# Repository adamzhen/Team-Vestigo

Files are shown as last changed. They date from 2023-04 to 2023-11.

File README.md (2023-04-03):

# Team-Vestigo

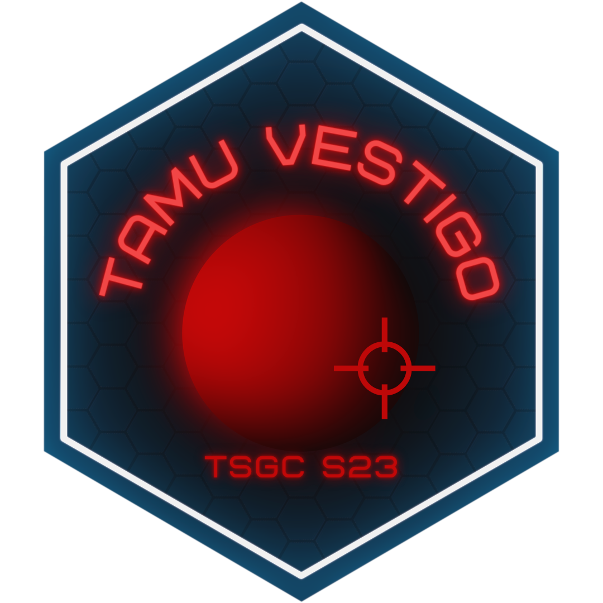
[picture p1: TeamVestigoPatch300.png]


### Crew Tracking for Space Analog Research

Since 2014, NASA’s Johnson Space Center has been using the Human Exploration Research Analog (HERA) to simulate manned space missions on Earth. We are currently developing an upgrade to HERA that will track the location and orientation of crew members in real-time, enabling researchers to efficiently analyze metrics such as how long crew members spent in certain areas or next to other crew members. The challenge is to design a device that not only has sufficient accuracy and battery life, but also a compact size and minimal crew interaction. This project is part of the Texas Space Grant Consortium Design Challenge.

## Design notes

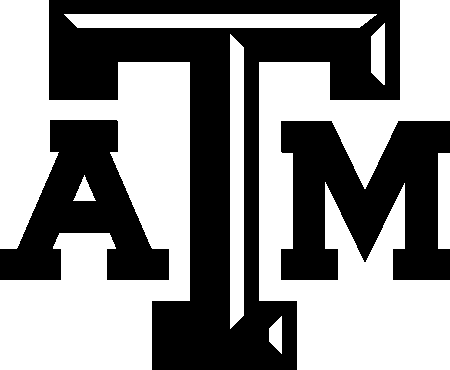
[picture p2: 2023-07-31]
PCB/TAMU(1).bmp

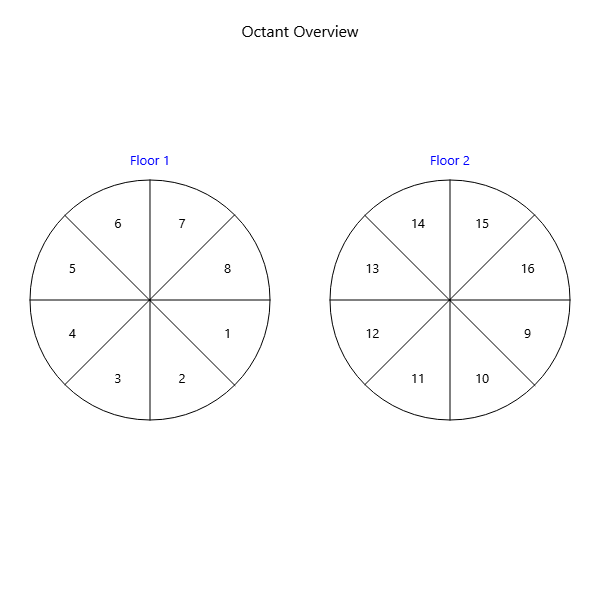
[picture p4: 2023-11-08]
GUI/QtDev/octant_reference.png

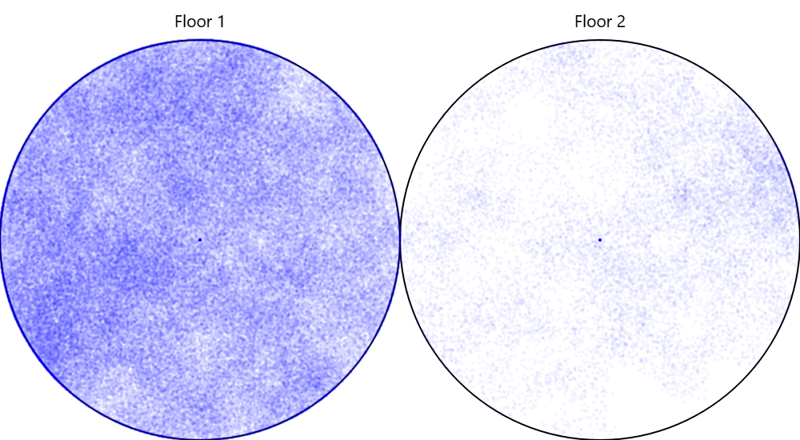
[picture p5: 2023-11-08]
GUI/QtDev/density_map.png

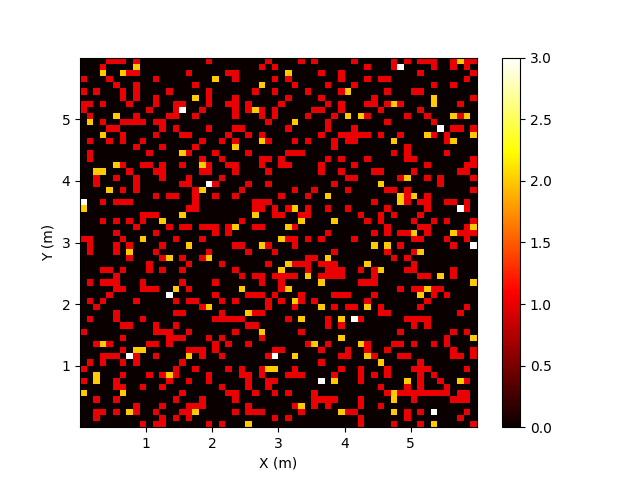
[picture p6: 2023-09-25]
GUI/QtDev/heatmap.png

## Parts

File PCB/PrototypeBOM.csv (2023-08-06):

Part | Value | Device | Package | Description | IOUT | PROD_ID | SF_ID | VALUE | VOUT
C1 | 1.0uF | 1.0UF-0402T-16V-10% | 0402-TIGHT | 1µF ceramic capacitors |  | CAP-12417 |  | 1.0uF
C2 | 0.1uF | 0.1UF-0402T-6.3V-10%-X7R | 0402-TIGHT | 0.1µF ceramic capacitors |  | CAP-14993 |  | 0.1uF
C3 | 0.1uF | C-0603 | C0603 | Ceramic Capacitors
C4 | 1.0uF | 1.0UF-0603-16V-10%-X7R | 0603 | 1µF ceramic capacitors |  | CAP-13930 |  | 1.0uF
C5 | 10uF | 10UF-0402T-6.3V-20% | 0402-TIGHT | 10.0µF ceramic capacitors |  | CAP-14848 |  | 10uF
C6 | 10uF | C-EUC0603 | C0603 | CAPACITOR, European symbol
C7 | 1.0uF | C-0603 | C0603 | Ceramic Capacitors
C8 | 10uF | C-0603 | C0603 | Ceramic Capacitors
C9 | 0.1uF | C-0603 | C0603 | Ceramic Capacitors
C10 | 1.0uF | 1.0UF-0402T-16V-10% | 0402-TIGHT | 1µF ceramic capacitors |  | CAP-12417 |  | 1.0uF
C11 | 0.1uF | C-0603 | C0603 | Ceramic Capacitors
C12 | 4.7uF | 4.7UF-0402_TIGHT-6.3V-20%-X5R | 0402-TIGHT | 4.7µF ceramic capacitors |  | CAP-14240 |  | 4.7uF
C13 | 0.1uF | 0.1UF-0402T-6.3V-10%-X7R | 0402-TIGHT | 0.1µF ceramic capacitors |  | CAP-14993 |  | 0.1uF
C14 | 0.1uF | C-0603 | C0603 | Ceramic Capacitors
C15 | 0.1uF | C-0603 | C0603 | Ceramic Capacitors
C19 | 4.7uF | 4.7UF-0603-35V-(20%) | 0603 | 4.7µF ceramic capacitors |  | CAP-14106 |  | 4.7uF
D1 | Yellow | LED-YELLOW0603 | LED-0603 | Yellow SMD LED |  | DIO-09003 |  | Yellow
D4 | 3A/10V/280mV | DIODE-SCHOTTKY-BAT60A | SOD-323 | Schottky diode |  | DIO-14072 |  | 3A/10V/280mV
D12 | RED | LED-RED0603 | LED-0603 | Red SMD LED |  | DIO-00819 |  | RED
J1 | USB Type C | USB_C_2-LAYER_PADS | USB-C-16P-2LAYER-PADS | USB Type C 16Pin Connector |  | CONN-14122
J3 | Connector | CONN_10";1X10" | Multi connection point. Often used as Generic Header-pin footprint for 0.1 inch spaced/style header connections |  | CONN-11563
J4 | Battery Connector | JST_2MM_MALE | JST-2-SMD | JST 2MM MALE RA CONNECTOR |  | CONN-11443 | PRT-08612
JP2 | JUMPER-SMT_2_NC_TRACE_SILK | JUMPER-SMT_2_NC_TRACE_SILK | SMT-JUMPER_2_NC_TRACE_SILK | Normally closed trace jumper
Q1 | S8050 | TRANSISTOR-NPN-SOT23 | SOT23 | NPN audion
Q3 | 20V/4.2A/52m?/1.4W | MOSFET_PCH-DMG2305UX-7 | SOT23-3@1 | P-channel MOSFETs |  | TRANS-14388 |  | 20V/4.2A/52m?/1.4W
Q4 | S8050 | TRANSISTOR-NPN-SOT23 | SOT23 | NPN audion
Q6 | 20V/0.2A/8MHz/1.2?/1Vth | MOSFET-NCH-RE1C002UN | SOT-416FL | N-channel MOSFETs |  | TRANS_14399 |  | 20V/0.2A/8MHz/1.2?/1Vth
Q8 | 20V/0.2A/8MHz/1.2?/1Vth | MOSFET-NCH-RE1C002UN | SOT-416FL | N-channel MOSFETs |  | TRANS_14399 |  | 20V/0.2A/8MHz/1.2?/1Vth
Q10 | 20V/0.2A/8MHz/1.2?/1Vth | MOSFET-NCH-RE1C002UN | SOT-416FL | N-channel MOSFETs |  | TRANS_14399 |  | 20V/0.2A/8MHz/1.2?/1Vth
Q12 | 20V/0.2A/8MHz/1.2?/1Vth | MOSFET-NCH-RE1C002UN | SOT-416FL | N-channel MOSFETs |  | TRANS_14399 |  | 20V/0.2A/8MHz/1.2?/1Vth
Q14 | 20V/0.2A/8MHz/1.2?/1Vth | MOSFET-NCH-RE1C002UN | SOT-416FL | N-channel MOSFETs |  | TRANS_14399 |  | 20V/0.2A/8MHz/1.2?/1Vth
Q16 | 20V/0.2A/8MHz/1.2?/1Vth | MOSFET-NCH-RE1C002UN | SOT-416FL | N-channel MOSFETs |  | TRANS_14399 |  | 20V/0.2A/8MHz/1.2?/1Vth
R1 | 1K | RESISTOR_0603_NOOUT | 0603-NO | Resistors
R3 | 1k | 1KOHM-0402T-1/16W-1% | 0402-TIGHT | 1k? resistor |  | RES-14342 |  | 1k
R4 | 2.2k | 2.2KOHM-0402T-1/16W-1% | 0402-TIGHT | 2.2k? resistor |  | RES-14341 |  | 2.2k
R5 | 2.2k | 2.2KOHM-0402T-1/16W-1% | 0402-TIGHT | 2.2k? resistor |  | RES-14341 |  | 2.2k
R6 | 2.0k | 2.0KOHM-0603-1/10W-5% | 0603 | 2k? resistor |  | RES-08296 |  | 2.0k
R7 | 10k | 10KOHM-0402T-1/16W-1% | 0402-TIGHT | 10k? resistor |  | RES-14241 |  | 10k
R8 | 10k | 10KOHM-0402T-1/16W-1% | 0402-TIGHT | 10k? resistor |  | RES-14241 |  | 10k
R9 | 5.1k | 5.1KOHM-0402T-1/16W-1% | 0402-TIGHT |  |  | RES-14340 |  | 5.1k
R10 | 5.1k | 5.1KOHM-0402T-1/16W-1% | 0402-TIGHT |  |  | RES-14340 |  | 5.1k
R11 | 1K | R-0603 | 0603
R12 | 1K | R-0603 | 0603
R13 | 1K | RESISTOR_0603_NOOUT | 0603-NO | Resistors
R14 | 1K | RESISTOR_0603_NOOUT | 0603-NO | Resistors
R15 | 10K | RESISTOR_0603_NOOUT | 0603-NO | Resistors
R16 | 2.2k | 2.2KOHM-0402T-1/16W-1% | 0402-TIGHT | 2.2k? resistor |  | RES-14341 |  | 2.2k
R17 | 2.2k | 2.2KOHM-0402T-1/16W-1% | 0402-TIGHT | 2.2k? resistor |  | RES-14341 |  | 2.2k
R18 | 2.2k | 2.2KOHM-0402T-1/16W-1% | 0402-TIGHT | 2.2k? resistor |  | RES-14341 |  | 2.2k
R19 | 2.2k | 2.2KOHM-0402T-1/16W-1% | 0402-TIGHT | 2.2k? resistor |  | RES-14341 |  | 2.2k
R20 | 2.2k | 2.2KOHM-0402T-1/16W-1% | 0402-TIGHT | 2.2k? resistor |  | RES-14341 |  | 2.2k
R21 | 2.2k | 2.2KOHM-0402T-1/16W-1% | 0402-TIGHT | 2.2k? resistor |  | RES-14341 |  | 2.2k
R22 | 2.2k | 2.2KOHM-0402T-1/16W-1% | 0402-TIGHT | 2.2k? resistor |  | RES-14341 |  | 2.2k
R23 | 2.2k | 2.2KOHM-0402T-1/16W-1% | 0402-TIGHT | 2.2k? resistor |  | RES-14341 |  | 2.2k
R24 | 2.2k | 2.2KOHM-0402T-1/16W-1% | 0402-TIGHT | 2.2k? resistor |  | RES-14341 |  | 2.2k
R25 | 2.2k | 2.2KOHM-0402T-1/16W-1% | 0402-TIGHT | 2.2k? resistor |  | RES-14341 |  | 2.2k
R34 | 1k | 1KOHM-0402T-1/16W-1% | 0402-TIGHT | 1k? resistor |  | RES-14342 |  | 1k
TP1 | 1.8V | TEST-POINT3 | PAD.03X.03 | SparkFun Test Points
U1 | 9DoF IMU | ICM-20948 | QFN24-3X3 | ICM-20948 9 Degree of Freedom IMU |  | IC-14247 |  | 9DoF IMU
U2 | MCP73831 | MCP73831 | SOT23-5 | MCP73831T Li-Ion, Li-Pol Controller |  | IC-09995
U3 | ESP-WROOM-32 | ESP-WROOM-32 | ESP-WROOM-32
U5 | DWM1000 | DWM1000 | DWM1000
U6 | 1.8V/100mA | V_REG_SP6214-1.8V | SC70 | Voltage Regulator - SP6214 |  | VREG-08428 |  | 1.8V/100mA
U7 | CH340C | CH340C | SO016 |  |  | IC-14038
U8 | XC6222B331MR-G | XC6222B331MR-G | SOT23-5 |  | 700mA | VREG-16775 |  |  | 3.3V

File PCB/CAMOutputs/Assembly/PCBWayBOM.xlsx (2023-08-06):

Item # | *Designator | *Qty | Manufacturer | *Mfg Part # | Description / Value | *Package/Footprint | Type | Your Instructions / Notes
1 | C8, C9, C3, C7, C10, C14, C15 | 7 | KYOCERA AVX | KGM15AR71C104KT | Multilayer Ceramic Capacitors MLCC - SMD/SMT 16V .1uF X7R 0603 10% | 0603 | SMD
2 | C6 | 1 | TDK | CGA3E1X7R1C105K080AC | Multilayer Ceramic Capacitors MLCC - SMD/SMT CGA 0603 16V 1uF X7R 10% AEC-Q200 | 0603 | SMD
3 | U$6, U$9 | 2 | Everlight Elec | 19-217/GHC-YR1S2/3T | Colorless transparence -40℃~+85℃ 520nm~535nm Emerald 120° 110mW 0603 Light Emitting Diodes (LED) ROHS | 0603 | SMD
4 | Q2, Q5, Q6, Q7, Q8, Q10 | 6 | ROHM Semiconductor | RE1C002UNTCL | MOSFET 1.2V Drive Nch MOSFET | SOT-416FL | SMD
5 | Q3 | 1 | Diodes Incorporated | DMG2305UX-7 | MOSFET P-Ch ENH FET -20V 52mOh -5A | SOT-23-3 | SMD
6 | D1 | 1 | Infineon Technologies | BAT60AE6327HTSA1 | Schottky Diodes & Rectifiers 10 V 3000 mA | SOD-323-2 | SMD
7 | U$11 | 1 | WCH(Jiangsu Qin Heng) | CH340B | 2Mbps Transceiver USB 2.0 SOP-16 USB ICs ROHS | SOP-16 | SMD
8 | C2, C4, C11 | 3 | Murata Electronics | GRM188R61A106ME69D | Multilayer Ceramic Capacitors MLCC - SMD/SMT 10 uF 10 VDC 20% 0603 X5R | 0603 | SMD
9 | C1,C5, C12, C16 | 4 | Wurth Elektronik | 885012000000 | Multilayer Ceramic Capacitors MLCC - SMD/SMT WCAP-CSGP 2.2uF 16V 10% | 0603 | SMD
10 | C13, C17, C19 | 3 | Murata Electronics | GRT188C81C475KE13D | Multilayer Ceramic Capacitors MLCC - SMD/SMT 4.7 uF 16 VDC 10% 0603 X6S AEC-Q200 | 0603 | SMD
11 | U5 | 1 | Qorvo | DWM3000TR13 | RF Modules UWB XCVR Module | 24 Pin 23 x 13 mm side castellated package | SMD
12 | U3 | 1 | Espressif Systems | ESP32-WROOM-32D-N4 | Multiprotocol Modules SMD Module, ESP32-D0WD, 32Mbits SPI flash, UART mode, PCB antenna | (18.00±0.10) × (25.50±0.10) × (3.10±0.10) 38 Pin Package | SMD
13 | U$5 | 1 | HEERMICR | HEERMICR | SOT-23-6 DC-DC Converters ROHS | SOT-23-6 | SMD
14 | U$12 | 1 | TDK InvenSense | ICM-20948 | IMUs - Inertial Measurement Units World's Lowest Power 9-Axis MEMS MotionTracking Device |  | QFN-24
15 | U$1, U$3 | 2 | Korean Hroparts Elec | K2-6639SP-C4SC-04 | 50mA Brick nogging SPST 100MΩ 1000000 times 250gf@±30gf 12V SMD Tactile Switches ROHS | Button | SMD
16 | U2 | 1 | Microchip Technology | MCP73831T-2ATI/OT | Battery Management Charge mgnt contr | SOT-23-5 | SMD
17 | U$2 | 1 | TDK | MLZ2012M100WT000 | Power Inductors - SMD 10 UH 20% | 805 | SMD
18 | R11, R15 | 2 | Vishay / Dale | CRCW040210K0FKEDC | Thick Film Resistors - SMD 1/16watt 10Kohms 1% Commercial Use | 0402 | SMD
19 | R9, R10, R14 | 3 | Panasonic | ERJ-3EKF1002V | Thick Film Resistors 0603 10Kohms 1% AEC-Q200 | 0603 | SMD
20 | R8 | 1 | Vishay / Draloric | RCA04021K00JNED | Thick Film Resistors - SMD RCA0402 1K0 5% 200 ET7 e3 | 0402 | SMD
21 | R1, R3, R13, R24, R25 | 5 | Panasonic | ERJ-3EKF1001V | Thick Film Resistors 0603 1Kohms 1% AEC-Q200 | 0603 | SMD
22 | R2, R4, R5, R16, R17, R18, R19, R20, R21, R22, R23, R29 | 12 | Bourns | CR0402-JW-222GLF | Thick Film Resistors - SMD 2.2K OHM 5% | 0402 | SMD
23 | R6 | 1 | Panasonic | ERJ-3EKF2001V | Thick Film Resistors - SMD 0603 2Kohms 1% AEC-Q200 | 0603 | SMD
24 | R7 | 1 | ROHM Semiconductor | SFR03EZPJ472 | Thick Film Resistors - SMD 0603 4.7Kohms 5% Anti-Sulfur AEC-Q200 | 0603 | SMD
25 | R12, R27 | 2 | Bourns | CR0402-FX-5101GLF | Thick Film Resistors - SMD 5.1K OHM 1% | 0402 | SMD
26 | Q1, Q4 | 2 | Micro Commercial Components (MCC) | MMS8050-H-TP | Bipolar Transistors - BJT NPN PURPOSE AMPLIFIER | SOT-23-3 | SMD
27 | U$8 | 1 | JST Sales America | SM02B-PASS-TB(LF)(SN) | 1x2P PA 1 2mm Male pin 2 -25℃~+85℃ 3A Surface Mount SMD,P=2mm Wire To Board / Wire To Wire Connector ROHS | SMD,P=2mm | SMD
28 | U$4 | 1 | Texas Instruments | TPS62202DBVR | Switching Voltage Regulators 1.8V Out Hi-Eff Step-Down Converter | SOT-23-5 | SMD
29 | U$7 | 1 | TECH PUBLIC | TPSMF05CT1G | SOT-323-6 | SOT-323-6 ESD Protection Devices ROHS | SMD
30 | U$10 | 1 | DEALON | USB-TYPE-C-019 | 3A 1 Surface Mount 16P Female -25℃~+85℃ Type-C SMD USB Connectors ROHS | USB-C Female Connector | SMD

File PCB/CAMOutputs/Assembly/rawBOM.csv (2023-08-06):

Qty Value Device Package Parts Description DESCRIPTION HEIGHT LCSC_DATASHEET LCSC_PART LCSC_PRICE1_EUR LCSC_ROTATION_CCW LCSC_STOCK MANUFACTURER_NAME MANUFACTURER_PART_NUMBER MOUSER_PART_NUMBER MOUSER_PRICE-STOCK PROD_ID PROPERTIES VALUE
8 CONN_01PTH_2MM 1X01_2MM J2 | J3 | J4 | J5 | J6 | J7 | J8 | J9 Single connection point. Often used as Generic Header-pin footprint for 0.1 inch spaced/style header connections
7 0.1uF 0.1UF-0603-25V-5% 0603 C8 | C9 0.1µF ceramic capacitors CAP-08604 0.1uF | C7 | C10 | C14 | C15 Capacitor General purpose SMD Capacitor https://datasheet.lcsc.com/lcsc/1809301912_YAGEO-CC0603KRX7R9BB104_C14663.pdf C14663 0 7111530 50V 100nF X7R ±10% 0603 ROHS
1 1.0uF 1.0UF-0603-16V-10%-X7R 0603 C6 1µF ceramic capacitors CAP-13930 1.0uF
2 19-217/GHC-YR1S2/3T 19-217/GHC-YR1S2/3T 19-217/GHC-YR1S2/3T U$6 | U$9
6 20V/0.2A/8MHz/1.2Ω/1Vth MOSFET-NCH-RE1C002UN SOT-416FL Q2 | Q5 | Q6 | Q7 | Q8 | Q10 N-channel MOSFETs TRANS_14399 20V/0.2A/8MHz/1.2Ω/1Vth
1 20V/4.2A/52mΩ/1.4W MOSFET_PCH-DMG2305UX-7 SOT23-3@1 Q3 P-channel MOSFETs TRANS-14388 20V/4.2A/52mΩ/1.4W
1 BAT60AE6327HTSA1 BAT60AE6327HTSA1 SOD2513X110N D1 INFINEON - BAT60AE6327HTSA1 - RECTIFIER | SCHOTTKY | 3A | 10V | SOD-323 INFINEON - BAT60AE6327HTSA1 - RECTIFIER | SCHOTTKY | 3A | 10V | SOD-323 1.1mm Infineon BAT60AE6327HTSA1 726-BAT60AE6327HTSA1 https://www.mouser.co.uk/ProductDetail/Infineon-Technologies/BAT60AE6327HTSA1?qs=OwbwYO03UsIW3Y2lCXbs8Q%3D%3D
1 CH340B CH340B SOP-16 U$11
3 C_10UF/10V_0603 C_10UF/10V_0603 C0603 C2 | C4 | C11 Capacitor General purpose SMD Capacitor https://datasheet.lcsc.com/lcsc/1810191219_Samsung-Electro-Mechanics-CL10A106KP8NNNC_C19702.pdf C19702 0 2089400 10V 10uF X5R ±10% 0603 ROHS
4 C_2.2UF/16V_0603 C_2.2UF/16V_0603 C0603 C1 | C5 | C12 | C16 Capacitor General purpose SMD Capacitor https://datasheet.lcsc.com/lcsc/1810271109_Samsung-Electro-Mechanics-CL10A225KO8NNNC_C23630.pdf C23630 0 1324345 16V 2.2uF X5R ±10% 0603 ROHS
3 C_4.7UF/16V_0603 C_4.7UF/16V_0603 C0603 C13 | C17 | C19 Capacitor General purpose SMD Capacitor https://datasheet.lcsc.com/lcsc/1810261514_Samsung-Electro-Mechanics-CL10A475KO8NNNC_C19666.pdf C19666 0 2027167 16V 4.7uF X5R ±10% 0603 ROHS
1 DWM1000 DWM1000 DWM1000 U5
1 ESP-WROOM-32 ESP-WROOM-32 ESP-WROOM-32 U3
1 HE9008M6R HE9008M6R HE9008M6R U$5
1 ICM20948 ICM20948 ICM20948 U$12
2 K2-6639SP-C4SC-04_C83206 K2-6639SP-C4SC-04_C83206 K2-6639SP-C4SC-04 U$1 | U$3 K2-6639SP-C4SC-04_C83206 button | https://datasheet.lcsc.com/lcsc/2108131530_Korean-Hroparts-Elec-K2-6639SP-C4SC-04_C83206.pdf
1 MCP73831 MCP73831 SOT23-5 U2 MCP73831T Li-Ion | Li-Pol Controller IC-09995
1 MLF2012 MLF2012 MLF2012 U$2 MLF2012
2 R_10K_0402 R_10K_0402 R0402 R11 | R15 Resistor General purpose SMD Resistor https://datasheet.lcsc.com/lcsc/2110260030_UNI-ROYAL-Uniroyal-Elec-0402WGF1002TCE_C25744.pdf C25744 0 11564817 ±1% 1/16W Thick Film Resistors 50V ±100ppm -55°C~+155°C 10kOhm 0402 ROHS
3 R_10K_0603 R_10K_0603 R0603 R9 | R10 | R14 Resistor General purpose SMD Resistor https://datasheet.lcsc.com/lcsc/2110260030_UNI-ROYAL-Uniroyal-Elec-0603WAF1002T5E_C25804.pdf C25804 0 7979018 ±1% 1/10W Thick Film Resistors 75V ±100ppm -55°C~+155°C 10kOhm 0603 ROHS
1 R_1K_0402 R_1K_0402 R0402 R8 Resistor General purpose SMD Resistor https://datasheet.lcsc.com/lcsc/2110251730_UNI-ROYAL-Uniroyal-Elec-0402WGF1001TCE_C11702.pdf C11702 0 3758383 ±1% 1/16W Thick Film Resistors 50V ±100ppm -55°C~+155°C 1kOhm 0402 ROHS
5 R_1K_0603 R_1K_0603 R0603 R1 | R3 | R13 | R24 | R25 Resistor General purpose SMD Resistor https://datasheet.lcsc.com/lcsc/2110252030_UNI-ROYAL-Uniroyal-Elec-0603WAF1001T5E_C21190.pdf C21190 0 5175299 ±1% 1/10W Thick Film Resistors 75V ±100ppm -55°C~+155°C 1kOhm 0603 ROHS
12 R_2.2K_0402 R_2.2K_0402 R0402 R2 | R4 | R5 | R16 | R17 | R18 | R19 | R20 | R21 | R22 | R23 | R29 Resistor General purpose SMD Resistor https://datasheet.lcsc.com/lcsc/2110260030_UNI-ROYAL-Uniroyal-Elec-0402WGF2201TCE_C25879.pdf C25879 0 387501 ±1% 1/16W Thick Film Resistors 50V ±100ppm -55°C~+155°C 2.2kOhm 0402 ROHS
1 R_2K_0603 R_2K_0603 R0603 R6 Resistor General purpose SMD Resistor https://datasheet.lcsc.com/lcsc/2110252130_UNI-ROYAL-Uniroyal-Elec-0603WAF2001T5E_C22975.pdf C22975 0 3372290 ±1% 1/10W Thick Film Resistors 75V ±100ppm -55°C~+155°C 2kOhm 0603 ROHS
1 R_4.7K_0603 R_4.7K_0603 R0603 R7 Resistor General purpose SMD Resistor https://datasheet.lcsc.com/lcsc/2110252130_UNI-ROYAL-Uniroyal-Elec-0603WAF4701T5E_C23162.pdf C23162 0 3103173 ±1% 1/10W Thick Film Resistors 75V ±100ppm -55°C~+155°C 4.7kOhm 0603 ROHS
2 R_5.1K_0402 R_5.1K_0402 R0402 R12 | R27 Resistor General purpose SMD Resistor https://datasheet.lcsc.com/lcsc/2110260030_UNI-ROYAL-Uniroyal-Elec-0402WGF5101TCE_C25905.pdf C25905 0 1228443 ±1% 1/16W Thick Film Resistors 50V ±100ppm -55°C~+155°C 5.1kOhm 0402 ROHS
2 S8050 TRANSISTOR-NPN-SOT23 SOT23 Q1 | Q4 NPN audion
1 SM02B_PASS_TB_LF SM02B_PASS_TB_LF SM02B_PASS_TB_LF U$8
1 TPS62202DBVR TPS62202DBVR TPS62202DBVR U$4
1 TPSMF05CT1G TPSMF05CT1G TPSMF05CT1G U$7
1 USBC19 USBC19 USBC19 U$10

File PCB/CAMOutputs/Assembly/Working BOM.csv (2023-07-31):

COMMENT | DESIGNATOR | FOOTPRINT | JLCPCB ID | Qty Value Device Package Parts Description DESCRIPTION HEIGHT LCSC_DATASHEET LCSC_PART LCSC_PRICE1_EUR LCSC_ROTATION_CCW LCSC_STOCK MANUFACTURER_NAME MANUFACTURER_PART_NUMBER MOUSER_PART_NUMBER MOUSER_PRICE-STOCK PROD_ID PROPERTIES VALUE | Qty Value Device Package Parts Description DESCRIPTION HEIGHT LCSC_DATASHEET LCSC_PART LCSC_PRICE1_EUR LCSC_ROTATION_CCW LCSC_STOCK MANUFACTURER_NAME MANUFACTURER_PART_NUMBER MOUSER_PART_NUMBER MOUSER_PRICE-STOCK PROD_ID PROPERTIES VALUE
Single connection point. Often used as Generic Header-pin footprint for 0.1 inch spaced/style header connections | J2 | 1X01_2MM |  | 8;"";"CONN_01PTH_2MM";"1X01_2MM";"J2 | 8 CONN_01PTH_2MM 1X01_2MM J2, J3, J4, J5, J6, J7, J8, J9 Single connection point. Often used as Generic Header-pin footprint for 0.1 inch spaced/style header connections
Single connection point. Often used as Generic Header-pin footprint for 0.1 inch spaced/style header connections | J3 | 1X01_2MM |  | 2;"0.1uF";"0.1UF-0603-25V-5%";"0603";"C8 | 2 0.1uF 0.1UF-0603-25V-5% 0603 C8, C9 0.1µF ceramic capacitors CAP-08604 0.1uF
Single connection point. Often used as Generic Header-pin footprint for 0.1 inch spaced/style header connections | J4 | 1X01_2MM |  | 1;"1.0uF";"1.0UF-0603-16V-10%-X7R";"0603";"C6";"1ÂµF ceramic capacitors";"";"";"";"";"";"";"";"";"";"";"";"CAP-13930";"";"1.0uF"; | 1 1.0uF 1.0UF-0603-16V-10%-X7R 0603 C6 1µF ceramic capacitors CAP-13930 1.0uF
Single connection point. Often used as Generic Header-pin footprint for 0.1 inch spaced/style header connections | J5 | 1X01_2MM |  | 2;"19-217/GHC-YR1S2/3T";"19-217/GHC-YR1S2/3T";"19-217/GHC-YR1S2/3T";"U$6 | 2 19-217/GHC-YR1S2/3T 19-217/GHC-YR1S2/3T 19-217/GHC-YR1S2/3T U$6, U$9
Single connection point. Often used as Generic Header-pin footprint for 0.1 inch spaced/style header connections | J6 | 1X01_2MM |  | 6;"20V/0.2A/8MHz/1.2Î©/1Vth";"MOSFET-NCH-RE1C002UN";"SOT-416FL";"Q2 | 6 20V/0.2A/8MHz/1.2?/1Vth MOSFET-NCH-RE1C002UN SOT-416FL Q2, Q5, Q6, Q7, Q8, Q10 N-channel MOSFETs TRANS_14399 20V/0.2A/8MHz/1.2?/1Vth
Single connection point. Often used as Generic Header-pin footprint for 0.1 inch spaced/style header connections | J7 | 1X01_2MM |  | 1;"20V/4.2A/52mÎ©/1.4W";"MOSFET_PCH-DMG2305UX-7";"SOT23-3@1";"Q3";"P-channel MOSFETs";"";"";"";"";"";"";"";"";"";"";"";"TRANS-14388";"";"20V/4.2A/52mÎ©/1.4W"; | 1 20V/4.2A/52m?/1.4W MOSFET_PCH-DMG2305UX-7 SOT23-3@1 Q3 P-channel MOSFETs TRANS-14388 20V/4.2A/52m?/1.4W
Single connection point. Often used as Generic Header-pin footprint for 0.1 inch spaced/style header connections | J8 | 1X01_2MM |  | 1;"9DoF IMU";"ICM-20948";"QFN24-3X3";"U1";"ICM-20948 9 Degree of Freedom IMU";"";"";"";"";"";"";"";"";"";"";"";"IC-14247";"";"9DoF IMU"; | 1 9DoF IMU ICM-20948 QFN24-3X3 U1 ICM-20948 9 Degree of Freedom IMU IC-14247 9DoF IMU
Single connection point. Often used as Generic Header-pin footprint for 0.1 inch spaced/style header connections | J9 | 1X01_2MM |  | 1;"BAT60AE6327HTSA1";"BAT60AE6327HTSA1";"SOD2513X110N";"D1";"INFINEON - BAT60AE6327HTSA1 - RECTIFIER | 1 BAT60AE6327HTSA1 BAT60AE6327HTSA1 SOD2513X110N D1 INFINEON - BAT60AE6327HTSA1 - RECTIFIER, SCHOTTKY, 3A, 10V, SOD-323 INFINEON - BAT60AE6327HTSA1 - RECTIFIER, SCHOTTKY, 3A, 10V, SOD-323 1.1mm Infineon BAT60AE6327HTSA1 726-BAT60AE6327HTSA1 https://www.mouser.co.uk/ProductDetail/Infineon-Technologies/BAT60AE6327HTSA1?qs=OwbwYO03UsIW3Y2lCXbs8Q%3D%3D
19-217/GHC-YR1S2/3T | U$6 | 603 | C72043 | 1;"CH340C";"CH340C";"SO016";"U7";"";"";"";"";"";"";"";"";"";"";"";"";"IC-14038";"";""; | 1 CH340C CH340C SO016 U7 IC-14038
19-217/GHC-YR1S2/3T | U$9 | 603 | C72043 | 5;"C_100NF/50V_0603";"C_100NF/50V_0603";"C0603";"C3 | 5 C_100NF/50V_0603 C_100NF/50V_0603 C0603 C3, C7, C10, C14, C15 Capacitor General purpose SMD Capacitor https://datasheet.lcsc.com/lcsc/1809301912_YAGEO-CC0603KRX7R9BB104_C14663.pdf C14663 0 7111530 50V 100nF X7R ±10% 0603 ROHS
RE1C002UNTL | Q2 | SOT-416FL | C509959 | 3;"C_10UF/10V_0603";"C_10UF/10V_0603";"C0603";"C2 | 3 C_10UF/10V_0603 C_10UF/10V_0603 C0603 C2, C4, C11 Capacitor General purpose SMD Capacitor https://datasheet.lcsc.com/lcsc/1810191219_Samsung-Electro-Mechanics-CL10A106KP8NNNC_C19702.pdf C19702 0 2089400 10V 10uF X5R ±10% 0603 ROHS
RE1C002UNTL | Q5 | SOT-416FL | C509959 | 4;"C_2.2UF/16V_0603";"C_2.2UF/16V_0603";"C0603";"C1 | 4 C_2.2UF/16V_0603 C_2.2UF/16V_0603 C0603 C1, C5, C12, C16 Capacitor General purpose SMD Capacitor https://datasheet.lcsc.com/lcsc/1810271109_Samsung-Electro-Mechanics-CL10A225KO8NNNC_C23630.pdf C23630 0 1324345 16V 2.2uF X5R ±10% 0603 ROHS
RE1C002UNTL | Q6 | SOT-416FL | C509959 | 3;"C_4.7UF/16V_0603";"C_4.7UF/16V_0603";"C0603";"C13 | 3 C_4.7UF/16V_0603 C_4.7UF/16V_0603 C0603 C13, C17, C19 Capacitor General purpose SMD Capacitor https://datasheet.lcsc.com/lcsc/1810261514_Samsung-Electro-Mechanics-CL10A475KO8NNNC_C19666.pdf C19666 0 2027167 16V 4.7uF X5R ±10% 0603 ROHS
RE1C002UNTL | Q7 | SOT-416FL | C509959 | 1;"DWM1000";"DWM1000";"DWM1000";"U5";"";"";"";"";"";"";"";"";"";"";"";"";"";"";""; | 1 DWM1000 DWM1000 DWM1000 U5
RE1C002UNTL | Q8 | SOT-416FL | C509959 | 1;"ESP-WROOM-32";"ESP-WROOM-32";"ESP-WROOM-32";"U3";"";"";"";"";"";"";"";"";"";"";"";"";"";"";""; | 1 ESP-WROOM-32 ESP-WROOM-32 ESP-WROOM-32 U3
RE1C002UNTL | Q10 | SOT-416FL | C509959 | 1;"HE9008M6R";"HE9008M6R";"HE9008M6R";"U$5";"";"";"";"";"";"";"";"";"";"";"";"";"";"";""; | 1 HE9008M6R HE9008M6R HE9008M6R U$5
DMG2305UX-7 | Q3 | SOT-23 | C150470 | 2;"K2-6639SP-C4SC-04_C83206";"K2-6639SP-C4SC-04_C83206";"K2-6639SP-C4SC-04";"U$1 | 2 K2-6639SP-C4SC-04_C83206 K2-6639SP-C4SC-04_C83206 K2-6639SP-C4SC-04 U$1, U$3 K2-6639SP-C4SC-04_C83206 button, https://datasheet.lcsc.com/lcsc/2108131530_Korean-Hroparts-Elec-K2-6639SP-C4SC-04_C83206.pdf
CH340C | U7 | SOP-16 | C84681 | 1;"MCP73831";"MCP73831";"SOT23-5";"U2";"MCP73831T Li-Ion | 1 MCP73831 MCP73831 SOT23-5 U2 MCP73831T Li-Ion, Li-Pol Controller IC-09995
FCC0603F104Z500CT | C3 | 603 | C5137469 | 1;"MLF2012";"MLF2012";"MLF2012";"U$2";"MLF2012";"";"";"";"";"";"";"";"";"";"";"";"";"";""; | 1 MLF2012 MLF2012 MLF2012 U$2 MLF2012
FCC0603F104Z500CT | C7 | 603 | C5137469 | 2;"R_10K_0402";"R_10K_0402";"R0402";"R11 | 2 R_10K_0402 R_10K_0402 R0402 R11, R15 Resistor General purpose SMD Resistor https://datasheet.lcsc.com/lcsc/2110260030_UNI-ROYAL-Uniroyal-Elec-0402WGF1002TCE_C25744.pdf C25744 0 11564817 ±1% 1/16W Thick Film Resistors 50V ±100ppm -55°C~+155°C 10kOhm 0402 ROHS
FCC0603F104Z500CT | C8 | 603 | C5137469 | 3;"R_10K_0603";"R_10K_0603";"R0603";"R9 | 3 R_10K_0603 R_10K_0603 R0603 R9, R10, R14 Resistor General purpose SMD Resistor https://datasheet.lcsc.com/lcsc/2110260030_UNI-ROYAL-Uniroyal-Elec-0603WAF1002T5E_C25804.pdf C25804 0 7979018 ±1% 1/10W Thick Film Resistors 75V ±100ppm -55°C~+155°C 10kOhm 0603 ROHS
FCC0603F104Z500CT | C10 | 603 | C5137469 | 1;"R_1K_0402";"R_1K_0402";"R0402";"R8";"Resistor General purpose SMD Resistor";"";"";"https://datasheet.lcsc.com/lcsc/2110251730_UNI-ROYAL-Uniroyal-Elec-0402WGF1001TCE_C11702.pdf";"C11702";"";"0";"3758383";"";"";"";"";"";"Â±1% 1/16W Thick Film Resistors 50V Â±100ppm -55Â°C~+155Â°C 1kOhm 0402 ROHS";""; | 1 R_1K_0402 R_1K_0402 R0402 R8 Resistor General purpose SMD Resistor https://datasheet.lcsc.com/lcsc/2110251730_UNI-ROYAL-Uniroyal-Elec-0402WGF1001TCE_C11702.pdf C11702 0 3758383 ±1% 1/16W Thick Film Resistors 50V ±100ppm -55°C~+155°C 1kOhm 0402 ROHS
FCC0603F104Z500CT | C14 | 603 | C5137469 | 5;"R_1K_0603";"R_1K_0603";"R0603";"R1 | 5 R_1K_0603 R_1K_0603 R0603 R1, R3, R13, R24, R25 Resistor General purpose SMD Resistor https://datasheet.lcsc.com/lcsc/2110252030_UNI-ROYAL-Uniroyal-Elec-0603WAF1001T5E_C21190.pdf C21190 0 5175299 ±1% 1/10W Thick Film Resistors 75V ±100ppm -55°C~+155°C 1kOhm 0603 ROHS
FCC0603F104Z500CT | C15 | 603 | C5137469 | 12;"R_2.2K_0402";"R_2.2K_0402";"R0402";"R2 | 12 R_2.2K_0402 R_2.2K_0402 R0402 R2, R4, R5, R16, R17, R18, R19, R20, R21, R22, R23, R29 Resistor General purpose SMD Resistor https://datasheet.lcsc.com/lcsc/2110260030_UNI-ROYAL-Uniroyal-Elec-0402WGF2201TCE_C25879.pdf C25879 0 387501 ±1% 1/16W Thick Film Resistors 50V ±100ppm -55°C~+155°C 2.2kOhm 0402 ROHS
FCC0603F104Z500CT | C9 | 603 | C5137469 | 1;"R_2K_0603";"R_2K_0603";"R0603";"R6";"Resistor General purpose SMD Resistor";"";"";"https://datasheet.lcsc.com/lcsc/2110252130_UNI-ROYAL-Uniroyal-Elec-0603WAF2001T5E_C22975.pdf";"C22975";"";"0";"3372290";"";"";"";"";"";"Â±1% 1/10W Thick Film Resistors 75V Â±100ppm -55Â°C~+155Â°C 2kOhm 0603 ROHS";""; | 1 R_2K_0603 R_2K_0603 R0603 R6 Resistor General purpose SMD Resistor https://datasheet.lcsc.com/lcsc/2110252130_UNI-ROYAL-Uniroyal-Elec-0603WAF2001T5E_C22975.pdf C22975 0 3372290 ±1% 1/10W Thick Film Resistors 75V ±100ppm -55°C~+155°C 2kOhm 0603 ROHS
CC0603MRX5R6BB106 | C2 | 603 | C109453 | 1;"R_4.7K_0603";"R_4.7K_0603";"R0603";"R7";"Resistor General purpose SMD Resistor";"";"";"https://datasheet.lcsc.com/lcsc/2110252130_UNI-ROYAL-Uniroyal-Elec-0603WAF4701T5E_C23162.pdf";"C23162";"";"0";"3103173";"";"";"";"";"";"Â±1% 1/10W Thick Film Resistors 75V Â±100ppm -55Â°C~+155Â°C 4.7kOhm 0603 ROHS";""; | 1 R_4.7K_0603 R_4.7K_0603 R0603 R7 Resistor General purpose SMD Resistor https://datasheet.lcsc.com/lcsc/2110252130_UNI-ROYAL-Uniroyal-Elec-0603WAF4701T5E_C23162.pdf C23162 0 3103173 ±1% 1/10W Thick Film Resistors 75V ±100ppm -55°C~+155°C 4.7kOhm 0603 ROHS
CC0603MRX5R6BB106 | C4 | 603 | C109453 | 2;"R_5.1K_0402";"R_5.1K_0402";"R0402";"R12 | 2 R_5.1K_0402 R_5.1K_0402 R0402 R12, R27 Resistor General purpose SMD Resistor https://datasheet.lcsc.com/lcsc/2110260030_UNI-ROYAL-Uniroyal-Elec-0402WGF5101TCE_C25905.pdf C25905 0 1228443 ±1% 1/16W Thick Film Resistors 50V ±100ppm -55°C~+155°C 5.1kOhm 0402 ROHS
CC0603MRX5R6BB106 | C11 | 603 | C109453 | 2;"S8050";"TRANSISTOR-NPN-SOT23";"SOT23";"Q1 | 2 S8050 TRANSISTOR-NPN-SOT23 SOT23 Q1, Q4 NPN audion
EMK107BJ105KA-T | C6 | 603 | C87149 | 1;"SM02B_PASS_TB_LF";"SM02B_PASS_TB_LF";"SM02B_PASS_TB_LF";"U$8";"";"";"";"";"";"";"";"";"";"";"";"";"";"";""; | 1 SM02B_PASS_TB_LF SM02B_PASS_TB_LF SM02B_PASS_TB_LF U$8
CC0603MRX5R7BB225 | C1 | 603 | C2169170 | 1;"SMF05CT1G";"SMF05CT1G";"SOT65P210X110-6N";"IC1";"5-Line Transient Voltage Suppressor Array";"5-Line Transient Voltage Suppressor Array";"1.1mm";"";"";"";"";"";"onsemi";"SMF05CT1G";"863-SMF05CT1G";"https://www.mouser.co.uk/ProductDetail/onsemi/SMF05CT1G?qs=xZq1yRCsb1c8sZHBbx4IBw%3D%3D";"";"";""; | 1 SMF05CT1G SMF05CT1G SOT65P210X110-6N IC1 5-Line Transient Voltage Suppressor Array 5-Line Transient Voltage Suppressor Array 1.1mm onsemi SMF05CT1G 863-SMF05CT1G https://www.mouser.co.uk/ProductDetail/onsemi/SMF05CT1G?qs=xZq1yRCsb1c8sZHBbx4IBw%3D%3D
CC0603MRX5R7BB225 | C5 | 603 | C2169170 | 1;"TPS62202DBVR";"TPS62202DBVR";"TPS62202DBVR";"U$4";"";"";"";"";"";"";"";"";"";"";"";"";"";"";""; | 1 TPS62202DBVR TPS62202DBVR TPS62202DBVR U$4
CC0603MRX5R7BB225 | C12 | 603 | C2169170 | 1;"USBC19";"USBC19";"USBC19";"U$10";"";"";"";"";"";"";"";"";"";"";"";"";"";"";""; | 1 USBC19 USBC19 USBC19 U$10
CC0603MRX5R7BB225 | C16 | 603 | C2169170
0603X475K160CT | C13 | 603 | C296042
0603X475K160CT | C17 | 603 | C296042
0603X475K160CT | C19 | 603 | C296042
HE9008M6R | U$5 | SOT-23-6 | C5123432
K2-6639SP-C4SC-04 | U$1 | SMD | C83206
K2-6639SP-C4SC-04 | U$3 | SMD | C83206
MCP73831T-2ATI/OT | U2 | SOT-23-5 | C14879
MLF2012-100K | U$2 | 805 | C2941580
PTFR0402D10K0P9 | R11 | 402 | C375970
PTFR0402D10K0P9 | R15 | 402 | C375970
TNPW060310K0BETA | R9 | 603 | C3009396
TNPW060310K0BETA | R10 | 603 | C3009396
TNPW060310K0BETA | R14 | 603 | C3009396
CR0402F1K00Q10Z | R8 | 402 | C2835748
RT0603BRB071KL | R1 | 603 | C728580
RT0603BRB071KL | R3 | 603 | C728580
RT0603BRB071KL | R13 | 603 | C728580
RT0603BRB071KL | R24 | 603 | C728580
RT0603BRB071KL | R25 | 603 | C728580
SFR01MZPF2201 | R2 | 402 | C2085224
SFR01MZPF2201 | R4 | 402 | C2085224
SFR01MZPF2201 | R5 | 402 | C2085224
SFR01MZPF2201 | R16 | 402 | C2085224
SFR01MZPF2201 | R17 | 402 | C2085224
SFR01MZPF2201 | R18 | 402 | C2085224
SFR01MZPF2201 | R19 | 402 | C2085224
SFR01MZPF2201 | R20 | 402 | C2085224
SFR01MZPF2201 | R21 | 402 | C2085224
SFR01MZPF2201 | R22 | 402 | C2085224
SFR01MZPF2201 | R23 | 402 | C2085224
SFR01MZPF2201 | R29 | 402 | C2085224

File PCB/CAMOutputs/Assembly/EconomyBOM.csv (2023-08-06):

Comment | Designator | Footprint | JLCPCB Part #?optional?
CC0603MRX5R7BB225 | C12 | 603 | C2169170
0603X475K160CT | C13 | 603 | C296042
CC0603MRX5R7BB225 | C16 | 603 | C2169170
0603X475K160CT | C17 | 603 | C296042
0603X475K160CT | C19 | 603 | C296042
CC0603MRX5R7BB225 | C5 | 603 | C2169170
EMK107BJ105KA-T | C6 | 603 | C87149
FCC0603F104Z500CT | C7 | 603 | C5137469
FCC0603F104Z500CT | C9 | 603 | C5137469
RE1C002UNTL | Q10 | SOT-416FL | C509959
RE1C002UNTL | Q2 | SOT-416FL | C509959
DMG2305UX-7 | Q3 | SOT-23 | C150470
RE1C002UNTL | Q5 | SOT-416FL | C509959
RE1C002UNTL | Q6 | SOT-416FL | C509959
RE1C002UNTL | Q7 | SOT-416FL | C509959
RE1C002UNTL | Q8 | SOT-416FL | C509959
PTFR0402D10K0P9 | R11 | 402 | C375970
FRC0402J512 TS | R12 | 402 | C2906948
PTFR0402D10K0P9 | R15 | 402 | C375970
SFR01MZPF2201 | R16 | 402 | C2085224
SFR01MZPF2201 | R17 | 402 | C2085224
SFR01MZPF2201 | R18 | 402 | C2085224
SFR01MZPF2201 | R19 | 402 | C2085224
SFR01MZPF2201 | R2 | 402 | C2085224
SFR01MZPF2201 | R20 | 402 | C2085224
SFR01MZPF2201 | R21 | 402 | C2085224
SFR01MZPF2201 | R22 | 402 | C2085224
SFR01MZPF2201 | R23 | 402 | C2085224
WR06X102JTL | R24 | 603 | C384295
FRC0402J512 TS | R27 | 402 | C2906948
SFR01MZPF2201 | R29 | 402 | C2085224
WR06X102JTL | R3 | 603 | C384295
SFR01MZPF2201 | R4 | 402 | C2085224
SFR01MZPF2201 | R5 | 402 | C2085224
RTT03202JTP | R6 | 603 | C103396
RS-03K472JT | R7 | 603 | C88615
CR0402F1K00Q10Z | R8 | 402 | C2835748
K2-6639SP-C4SC-04 | U$1 | SMD | C83206
USB-TYPE-C-019 | U$10 | SMD | C2927039
CH340B | U$11 | SOP-16 | C81010
MLF2012-100K | U$2 | 805 | C2941580
K2-6639SP-C4SC-04 | U$3 | SMD | C83206
TPS62202DBVR | U$4 | SOT-23-5 | C9050
HE9008M6R | U$5 | SOT-23-6 | C5123432
19-217/GHC-YR1S2/3T | U$6 | 603 | C72043
TPSMF05CT1G | U$7 | SOT-323-6 | C558443
SM02B-PASS-TB(LF)(SN) | U$8 | SMD,P=2mm | C495198
19-217/GHC-YR1S2/3T | U$9 | 603 | C72043
MCP73831T-2ATI/OT | U2 | SOT-23-5 | C14879
ESP32-WROOM-32D-N4 | U3 | SMD,18x25.5mm | C473012

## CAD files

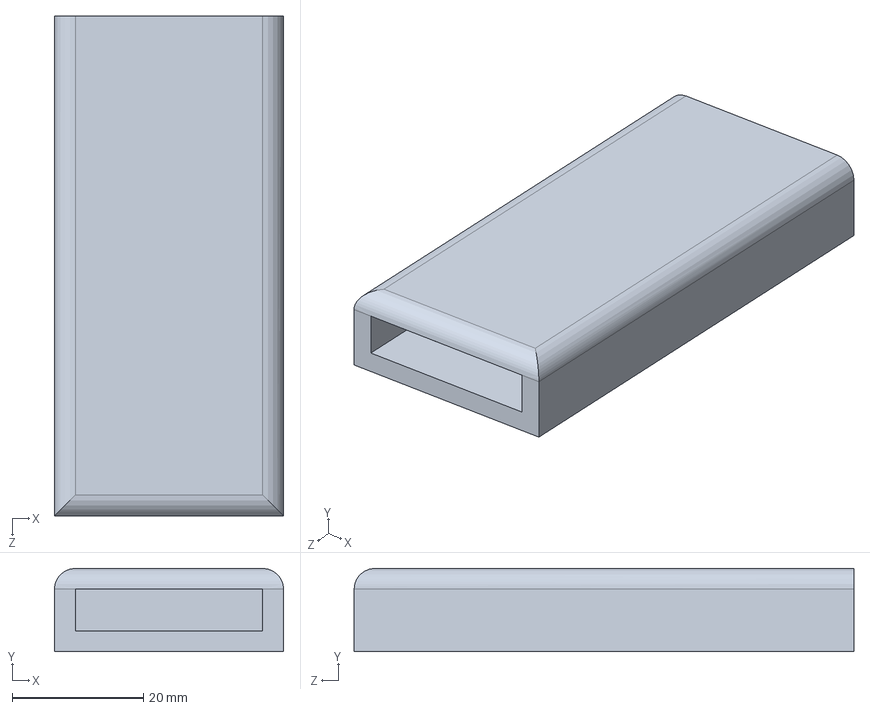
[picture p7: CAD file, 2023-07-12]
3D Models/Anchor on Top.SLDPRT
34.9 x 12.7 x 76.2 mm

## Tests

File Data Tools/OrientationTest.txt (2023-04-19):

3.52477	0.023808	298.601	20	20	18
3.52477	0.023808	298.623	20	20	18
3.52477	0.023808	298.603	20	20	18
3.51544	0.0277747	298.603	20	20	18
3.51763	-0.00142058	298.603	20	20	18
3.51763	-0.00142058	298.592	20	20	18
3.51763	-0.00142058	298.599	20	20	19
3.51763	-0.00142058	298.586	20	20	19
3.51763	-0.00142058	298.58	20	20	19
3.51763	-0.00142058	298.58	20	20	19
3.51763	-0.00142058	298.594	20	20	19
3.51763	-0.00142058	298.592	20	20	19
3.51763	-0.00142058	298.592	20	20	19
3.51763	-0.00142058	298.595	20	20	19
3.51763	-0.00142058	298.601	20	20	19
3.51009	0.0233529	298.592	20	20	19
3.51686	0.033769	298.613	20	20	19
3.51686	0.033769	298.613	20	20	19
3.51686	0.033769	298.641	20	20	20
3.51686	0.033769	298.641	20	20	20
3.51686	0.033769	298.651	20	20	20
3.51686	0.033769	298.654	20	20	20
3.51686	0.033769	298.623	20	20	20
3.51686	0.033769	298.599	20	20	20
3.51686	0.033769	298.599	20	20	20
3.51686	0.033769	298.616	20	20	20
3.51686	0.033769	298.629	20	20	20
3.51686	0.033769	298.631	20	20	20
3.51686	0.033769	298.621	20	20	20
3.51686	0.033769	298.621	20	20	20
3.51686	0.033769	298.614	20	20	20
3.51686	0.033769	298.608	20	20	21
3.51686	0.033769	298.62	20	20	21
3.46949	-0.0314988	298.633	20	20	21
3.46949	-0.0314988	298.633	20	20	21
3.46949	-0.0314988	298.653	20	20	21
3.4432	-0.0734727	298.653	20	20	21
3.4432	-0.0734727	298.653	20	20	21
3.4432	-0.0734727	298.653	20	20	21
3.4432	-0.0734727	298.646	20	20	21
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

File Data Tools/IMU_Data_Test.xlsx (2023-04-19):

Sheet: Test 1
 | roll | pitch | yaw | ax | ay | az
36 | 0.06 | 1.07 | 76.93 | -1.67 | -2.52 | 0.63
37 | 0.04 | 1.07 | 77.02 | 1.07 | 2.44 | -0.83
38 | 0.02 | 1.09 | 77.11 | -1.95 | 2.51 | 3.33 |  | Mean | St Dev | Variance
39 | 0.03 | 1.09 | 77.12 | 2.72 | -5 | 1.86 | roll | -0.06 | 0.03 | 0.001
40 | 0.03 | 1.1 | 77.09 | -0.12 | 3.82 | 0.4 | pitch | 1.17 | 0.03 | 0.001
41 | 0.03 | 1.1 | 77.09 | 1.1 | -5.22 | 3.33 | yaw | 77.35 | 0.08 | 0.006
42 | 0.03 | 1.1 | 77.09 | 1.84 | -3.02 | 3.82 | ax | -0.59 | 3.15 | 9.894
43 | 0.03 | 1.1 | 77.09 | 2.81 | -2.04 | 6.02 | ay | -0.03 | 3.09 | 9.532
44 | 0.03 | 1.1 | 77.09 | 1.59 | -4 | 4.8 | az | 2.24 | 3.13 | 9.792
45 | 0.03 | 1.1 | 77.11 | 0.18 | -4.47 | -8.88
46 | 0.03 | 1.1 | 77.12 | -2.94 | -5.89 | 3.82
47 | 0.03 | 1.1 | 77.12 | -2.7 | -2.22 | 4.31
48 | 0.03 | 1.1 | 77.12 | -2.21 | -1.98 | 1.62
49 | 0.03 | 1.1 | 77.12 | -0.01 | 1.44 | 5.04
50 | 0.03 | 1.1 | 77.12 | -4.89 | -2.96 | 7.48
51 | 0.03 | 1.11 | 77.14 | 2.59 | -3.03 | -2.04
52 | 0.03 | 1.1 | 77.17 | -3.72 | -1.3 | 4.31
53 | 0.03 | 1.1 | 77.17 | -0.06 | -1.3 | -2.04
54 | 0.03 | 1.1 | 77.17 | -1.77 | -1.54 | 4.31
55 | 0.03 | 1.1 | 77.17 | -3.48 | -2.28 | 2.35
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

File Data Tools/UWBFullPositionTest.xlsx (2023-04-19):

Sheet: Stationary
X (m) | Y (m) | Theta | HR | MIN | SEC |  |  |  |  |  | Anchors | X | Y | Error X | Error Y | Error Dist
3.42081 | 1.18505 | 287.486 | 19 | 40 | 58 |  |  |  |  |  | 1 | 0.1651 | 0.0508 | 0.00819 | 0.23735 | 0.23749126
3.42081 | 1.18505 | 287.486 | 19 | 40 | 58 |  |  |  |  |  | 2 | 5.0038 | 0.1778 | 0.00819 | 0.23735 | 0.23749126
3.42081 | 1.18505 | 287.455 | 19 | 40 | 59 |  | Actual | Mean | St Dev | Diff | 3 | 4.9784 | 3.81 | 0.00819 | 0.23735 | 0.23749126 |  | Mean | St Dev
3.42081 | 1.18505 | 287.455 | 19 | 40 | 59 | X | 3.429 | 3.405638617 | 0.1052343475 | -0.0233613832 | 4 | 0.1524 | 3.759 | 0.00819 | 0.23735 | 0.23749126 | Error X | 0.090 | 0.059
3.42081 | 1.18505 | 287.455 | 19 | 40 | 59 | Y | 1.4224 | 1.270855454 | 0.1429018713 | -0.1515445455 |  | 0.1651 | 0.0508 | 0.00819 | 0.23735 | 0.23749126 | Error Y | 0.166 | 0.126
3.42081 | 1.18505 | 287.455 | 19 | 40 | 59 |  |  |  |  | 0.1533346129 |  |  |  | 0.00819 | 0.23735 | 0.23749126 | Erro Dist | 0.206 | 0.111
3.42081 | 1.18505 | 287.466 | 19 | 40 | 59 |  |  |  |  |  |  |  |  | 0.00819 | 0.23735 | 0.23749126
3.42081 | 1.18505 | 287.445 | 19 | 40 | 59 |  |  |  |  |  |  |  |  | 0.00819 | 0.23735 | 0.23749126
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

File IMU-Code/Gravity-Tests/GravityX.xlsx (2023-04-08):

Ax | Ay | Az | Gx | Gy | Gz | Mx | My | Mz | A
-1003.66 | -0.73 | 15.87 | 0.42 | -0.49 | 0.05 | 0 | 0 | 0 | 1003.785727
-1005.62 | -0.24 | 10.74 | 0.66 | -0.38 | -0.06 | 0 | 0 | 0 | 1005.677378 |  | Mean | Expected | Diff | St Dev | Variance
-1002.69 | 1.22 | 6.1 | 0.44 | -0.45 | -0.03 | 0 | 0 | 0 | 1002.709297 | Ax | 1005.16 | 1000 | 5.16 | 3.029 | 9.172036537
-1008.06 | -4.64 | 5.62 | 0.63 | -0.53 | 0.12 | 0 | 0 | 0 | 1008.086344 | Ay | 5.54 | 0.00 | 5.54 | 4.187 | 17.53143519
-1009.77 | 2.2 | 6.84 | 0.14 | -0.5 | -0.05 | 0 | 0 | 0 | 1009.795563 | Az | 9.15 | 0.00 | 9.15 | 2.869 | 8.233454108
-1004.88 | -5.37 | 7.81 | 0.38 | -0.76 | 0.11 | 0 | 0 | 0 | 1004.924697 | A | 1005.23 | 1000.00 | 5.23 | 3.029 | 9.174051697
-1006.59 | -7.08 | 10.01 | 0.52 | -0.34 | -0.08 | 0 | 0 | 0 | 1006.664668 | Gx | 0.46 | 0.00 | 0.46 | 0.155 | 0.02393519205
-1009.77 | -2.2 | 12.94 | 0.31 | -0.43 | 0.18 | 0 | 0 | 0 | 1009.855305 | Gy | -0.49 | 0.00 | -0.49 | 0.148 | 0.02187725427
-1002.69 | -3.17 | 14.4 | 0.52 | -0.46 | -0.22 | 0 | 0 | 0 | 1002.798407 | Gz | 0.10 | 0.00 | 0.10 | 0.142 | 0.02020021621
-1007.57 | -4.64 | 7.08 | 0.6 | -0.66 | 0.19 | 0 | 0 | 0 | 1007.605558
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

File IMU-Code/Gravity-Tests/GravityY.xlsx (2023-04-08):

Ax | Ay | Az | Gx | Gy | Gz | Mx | My | Mz | A
7.81 | 991.46 | 5.62 | 0.65 | -0.3 | -0.11 | 0 | 0 | 0 | 991.5066879
3.42 | 986.08 | 7.81 | 0.4 | -0.18 | 0.16 | 0 | 0 | 0 | 986.1168586 |  | Mean | Expected | Diff | St Dev | Variance
5.37 | 989.5 | 11.23 | 0.28 | -0.47 | -0.12 | 0 | 0 | 0 | 989.5782939 | Ax | 4.97 | 0.00 | 4.97 | 3.044 | 9.263405441
11.47 | 987.3 | 11.96 | 0.47 | -0.29 | -0.08 | 0 | 0 | 0 | 987.4390576 | Ay | 988.04 | 1000.00 | -11.96 | 2.962 | 8.773208548
5.86 | 988.28 | 8.79 | 0.57 | -0.25 | -0.11 | 0 | 0 | 0 | 988.336462 | Az | 6.75 | 0.00 | 6.75 | 2.792 | 7.795290043
11.47 | 986.82 | 3.17 | 0.76 | 0.02 | 0.37 | 0 | 0 | 0 | 986.891748 | A | 988.08 | 1000.00 | -11.92 | 2.962 | 8.773162626
7.08 | 985.11 | 4.64 | 0.54 | -0.62 | 0.32 | 0 | 0 | 0 | 985.1463689 | Gx | 0.51 | 0.00 | 0.51 | 0.151 | 0.02273644574
5.86 | 989.75 | 7.81 | 0.31 | -0.15 | 0.05 | 0 | 0 | 0 | 989.7981603 | Gy | -0.36 | 0.00 | -0.36 | 0.139 | 0.01944527832
7.32 | 987.55 | 7.08 | 0.58 | -0.18 | 0.04 | 0 | 0 | 0 | 987.6025067 | Gz | 0.12 | 0.00 | 0.12 | 0.140 | 0.01957205234
5.62 | 989.75 | 8.79 | 0.52 | -0.38 | 0.24 | 0 | 0 | 0 | 989.8049863
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

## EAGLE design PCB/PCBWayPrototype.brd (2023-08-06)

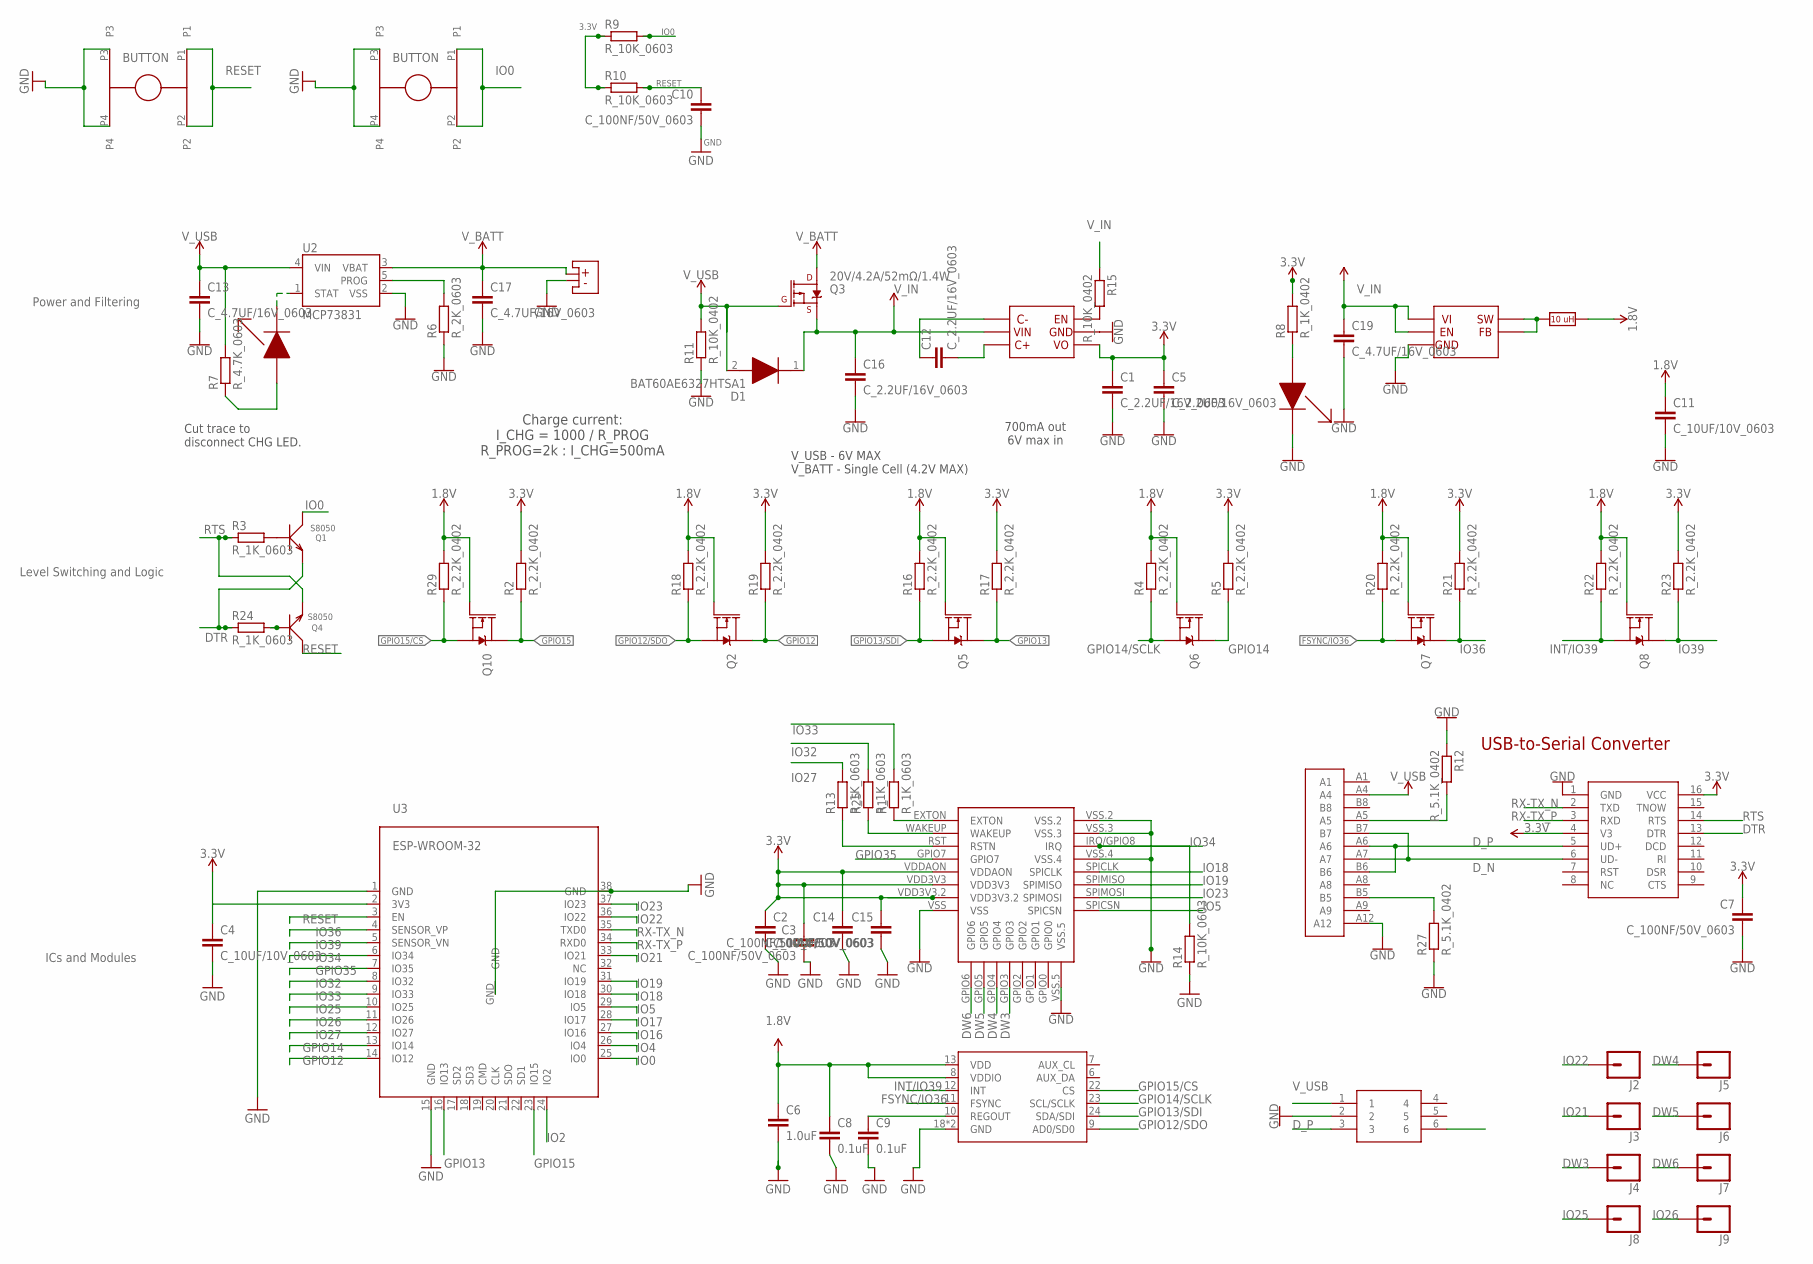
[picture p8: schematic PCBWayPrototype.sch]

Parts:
C1, C5, C12, C16: C_2.2UF/16V_0603; C0603
C2, C4, C11: C_10UF/10V_0603; C0603
C3, C7, C10, C14, C15: C_100NF/50V_0603; C0603
C6: 1.0uF; 0603
C8, C9: 0.1uF; 0603
C13, C17, C19: C_4.7UF/16V_0603; C0603
D1: BAT60AE6327HTSA1; SOD2513X110N
J2, J3, J4, J5, J6, J7, J8, J9: CONN_01PTH_2MM; 1X01_2MM
Q1, Q4: S8050; SOT23
Q2, Q5, Q6, Q7, Q8, Q10: 20V/0.2A/8MHz/1.2Ω/1Vth; SOT-416FL
Q3: 20V/4.2A/52mΩ/1.4W; SOT23-3@1
R1, R3, R13, R24, R25: R_1K_0603; R0603
R2, R4, R5, R16, R17, R18, R19, R20, R21, R22, R23, R29: R_2.2K_0402; R0402
R6: R_2K_0603; R0603
R7: R_4.7K_0603; R0603
R8: R_1K_0402; R0402
R9, R10, R14: R_10K_0603; R0603
R11, R15: R_10K_0402; R0402
R12, R27: R_5.1K_0402; R0402
U2: MCP73831; SOT23-5
U3: ESP-WROOM-32
U5: DWM1000
U$1, U$3: K2-6639SP-C4SC-04_C83206; K2-6639SP-C4SC-04
U$2: MLF2012
U$4: TPS62202DBVR
U$5: HE9008M6R
U$6, U$9: 19-217/GHC-YR1S2/3T
U$7: TPSMF05CT1G
U$8: SM02B_PASS_TB_LF
U$10: USBC19
U$11: CH340B; SOP-16
U$12: ICM20948

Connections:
1.8V: C6.1, C8.1, C11.1, Q2.1 (G), Q5.1 (G), Q6.1 (G), Q7.1 (G), Q8.1 (G), Q10.1 (G), R4.2, R16.2, R18.2, R20.2, R22.2, R29.2, U$2.2, U$12.8 (VDDIO), U$12.13 (VDD)
3.3V: C1.1, C2.1, C3.1, C4.1, C5.1, C7.1, C14.1, C15.1, R2.2, R5.2, R8.2, R9.1, R10.1, R17.2, R19.2, R21.2, R23.2, U3.2 (3V3), U5.VDD3V3, U5.VDD3V3.2, U5.VDDAON, U$5.VOUT (VO), U$11.4 (V3), U$11.16 (VCC)
CHG_LED: R7.1, U$6.2 (1)
DTR: Q1.2 (E), R24.1, U$11.13 (DTR)
DW3: J4.1, U5.GPIO3
DW4: J5.1, U5.GPIO4
DW5: J6.1, U5.GPIO5
DW6: J7.1, U5.GPIO6
D_N: U$7.6, U$10.A7, U$10.B7, U$11.6 (UD-)
D_P: U$7.3, U$10.A6, U$10.B6, U$11.5 (UD+)
FSYNC/IO36: Q7.2 (S), R20.1, U$12.11 (FSYNC)
GND: C1.2, C2.2, C3.2, C4.2, C5.2, C6.2, C7.2, C8.2, C9.2, C10.2, C11.2, C13.2, C14.2, C15.2, C16.2, C17.2, C19.2, R6.1, R11.1, R12.1, R14.1, R27.1, U2.2 (VSS), U3.1 (GND), U3.15 (GND), U3.38 (GND), U3.GND, U5.VSS, U5.VSS.2, U5.VSS.3, U5.VSS.4, U5.VSS.5, U$1.P3, U$1.P4, U$3.P3, U$3.P4, U$4.2 (GND), U$5.GND, U$7.2, U$8.3 (-), U$9.1 (2), U$10.A12, U$11.1 (GND), U$12.18 (GND), U$12.20 (GND)
GPIO12: Q2.3 (D), R19.1, U3.14 (IO12)
GPIO12/SDO: Q2.2 (S), R18.1, U$12.9 (AD0/SD0)
GPIO13: Q5.3 (D), R17.1, U3.16 (IO13)
GPIO13/SDI: Q5.2 (S), R16.1, U$12.24 (SDA/SDI)
GPIO14: Q6.3 (D), R5.1, U3.13 (IO14)
GPIO14/SCLK: Q6.2 (S), R4.1, U$12.23 (SCL/SCLK)
GPIO15: Q10.3 (D), R2.1, U3.23 (IO15)
GPIO15/CS: Q10.2 (S), R29.1, U$12.22 (CS)
GPIO35: U3.7 (IO35), U5.GPIO7
INT/IO39: Q8.2 (S), R22.1, U$12.12 (INT)
IO0: Q1.3 (C), R9.2, U3.25 (IO0), U$3.P1, U$3.P2
IO2: U3.24 (IO2)
IO4: U3.26 (IO4)
IO5: U3.29 (IO5), U5.SPICSN
IO16: U3.27 (IO16)
IO17: U3.28 (IO17)
IO18: U3.30 (IO18), U5.SPICLK
IO19: U3.31 (IO19), U5.SPIMISO
IO21: J3.1, U3.33 (IO21)
IO22: J2.1, U3.36 (IO22)
IO23: U3.37 (IO23), U5.SPIMOSI
IO25: J8.1, U3.10 (IO25)
IO26: J9.1, U3.11 (IO26)
IO27: R13.2, U3.12 (IO27)
IO32: R25.2, U3.8 (IO32)
IO33: R1.2, U3.9 (IO33)
IO34: R14.2, U3.6 (IO34), U5.IRQ/GPIO8 (IRQ)
IO36: Q7.3 (D), R21.1, U3.4 (SENSOR_VP)
IO39: Q8.3 (D), R23.1, U3.5 (SENSOR_VN)
unnamed: Q4.1 (B), R24.2
unnamed: Q1.1 (B), R3.2
unnamed: R6.2, U2.5 (PROG)
unnamed: R8.1, U$9.2 (1)
unnamed: U2.1 (STAT), U$6.1 (2)
unnamed: U$2.1, U$4.4 (FB), U$4.5 (SW)
unnamed: R15.2, U$5.EN
unnamed: R1.1, U5.EXTON
unnamed: R25.1, U5.WAKEUP
unnamed: R13.1, U5.RST (RSTN)
unnamed: C9.1, U$12.10 (REGOUT)
unnamed: C12.1, U$5.C-
unnamed: C12.2, U$5.C+
unnamed: R27.2, U$10.B5
unnamed: R12.2, U$10.A5
RESET: C10.1, Q4.3 (C), R10.2, U3.3 (EN), U$1.P1, U$1.P2
RTS: Q4.2 (E), R3.1, U$11.14 (RTS)
RX-TX_N: U3.35 (TXD0), U$11.2 (TXD)
RX-TX_P: U3.34 (RXD0), U$11.3 (RXD)
V_BATT: C17.1, Q3.3 (D), U2.3 (VBAT), U$8.4 (+)
V_IN: C16.1, C19.1, D1.1 (K), Q3.2 (S), R15.1, U$4.1 (VI), U$4.3 (EN), U$5.VIN
V_USB: C13.1, D1.2 (A), Q3.1 (G), R7.2, R11.2, U2.4 (VIN), U$7.1, U$10.A4

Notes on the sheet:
USB-to-Serial Converter
700mA out 6V max in
V_USB - 6V MAX V_BATT - Single Cell (4.2V MAX)
Charge current: I_CHG = 1000 / R_PROG R_PROG=2k : I_CHG=500mA
Cut trace to disconnect CHG LED.
Power and Filtering
Level Switching and Logic
ICs and Modules

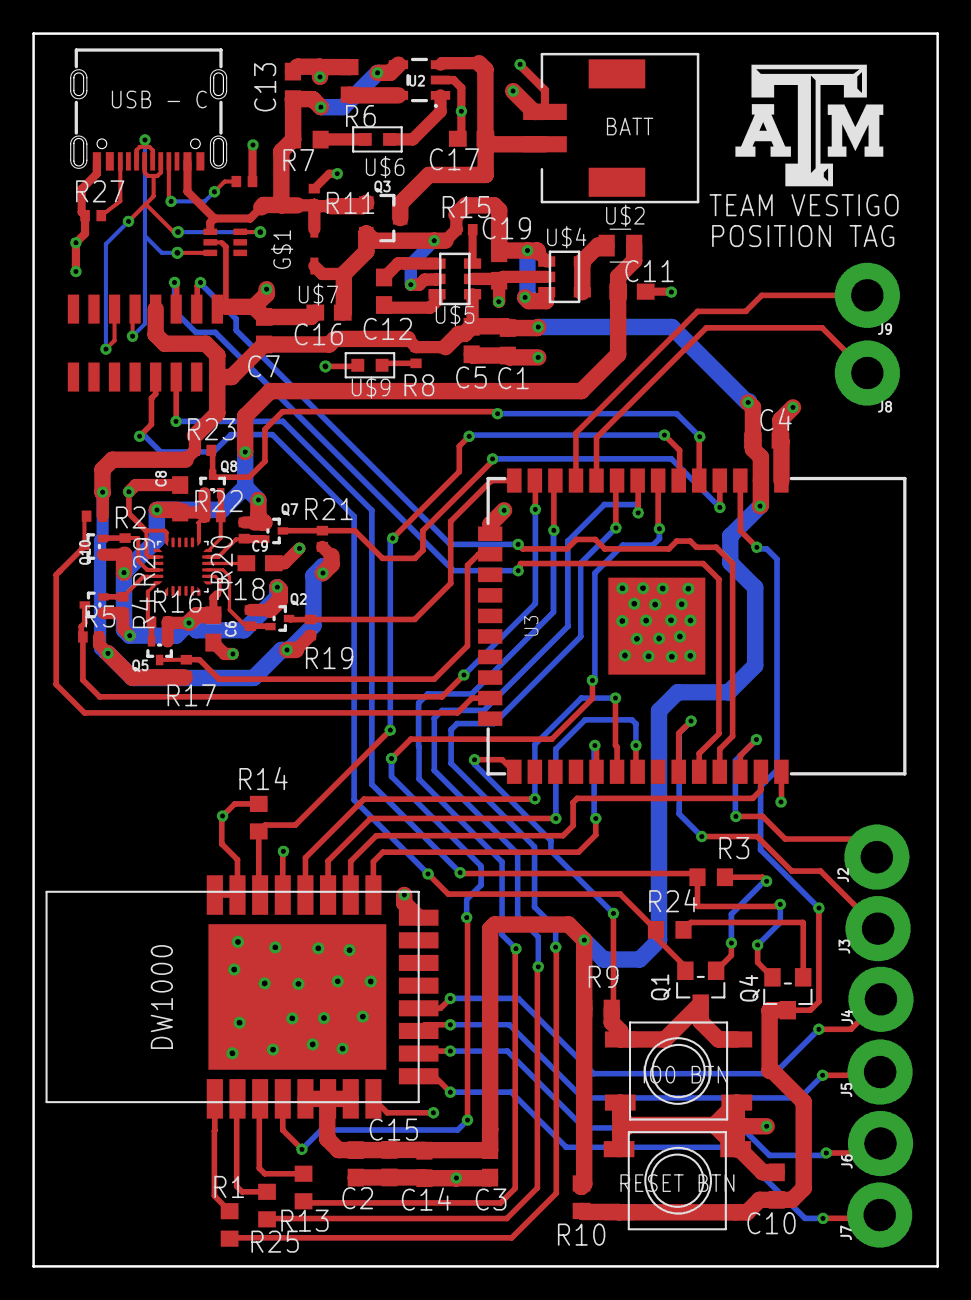
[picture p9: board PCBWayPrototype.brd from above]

Board: 4 copper layers, 55.9 x 76.2 mm, 78 parts (0 on the bottom side), 59 nets.

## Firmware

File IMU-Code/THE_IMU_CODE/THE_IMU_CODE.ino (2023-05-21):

/****************************************************************
 * Example6_DMP_Quat9_Orientation.ino
 * ICM 20948 Arduino Library Demo
 * Initialize the DMP based on the TDK InvenSense ICM20948_eMD_nucleo_1.0 example-icm20948
 * Paul Clark, April 25th, 2021
 * Based on original code by:
 * Owen Lyke @ SparkFun Electronics
 * Original Creation Date: April 17 2019
 * 
 * ** This example is based on InvenSense's _confidential_ Application Note "Programming Sequence for DMP Hardware Functions".
 * ** We are grateful to InvenSense for sharing this with us.
 * 
 * ** Important note: by default the DMP functionality is disabled in the library
 * ** as the DMP firmware takes up 14301 Bytes of program memory.
 * ** To use the DMP, you will need to:
 * ** Edit ICM_20948_C.h
 * ** Uncomment line 29: #define ICM_20948_USE_DMP
 * ** Save changes
 * ** If you are using Windows, you can find ICM_20948_C.h in:
 * ** Documents\Arduino\libraries\SparkFun_ICM-20948_ArduinoLibrary\src\util
 *
 * Please see License.md for the license information.
 *
 * Distributed as-is; no warranty is given.
 ***************************************************************/

#include "ICM_20948.h" // Click here to get the library: http://librarymanager/All#SparkFun_ICM_20948_IMU
#include <ArduinoJson.h>
#include <WiFiUdp.h>
#include <vector>
#include <math.h>
#include <WiFi.h>
#include <Wire.h> // Needed for I2C

#include <SparkFun_MAX1704x_Fuel_Gauge_Arduino_Library.h> // Click here to get the library: http://librarymanager/All#SparkFun_MAX1704x_Fuel_Gauge_Arduino_Library
SFE_MAX1704X lipo(MAX1704X_MAX17048); // Allow access to all the 17048 features

//#define USE_SPI       // Uncomment this to use SPI

#define QUAT_ANIMATION // Uncomment this line to output data in the correct format for ZaneL's Node.js Quaternion animation tool: https://github.com/ZaneL/quaternion_sensor_3d_nodejs
#define SERIAL_PORT Serial

#define SPI_PORT SPI // Your desired SPI port.       Used only when "USE_SPI" is defined
#define CS_PIN 2     // Which pin you connect CS to. Used only when "USE_SPI" is defined

#define WIRE_PORT Wire // Your desired Wire port.      Used when "USE_SPI" is not defined
// The value of the last bit of the I2C address.
// On the SparkFun 9DoF IMU breakout the default is 1, and when the ADR jumper is closed the value becomes 0
#define AD0_VAL 1
#define LED_PIN 13

//#define DEBUG // used for debugging
#define TRANSMIT
//#define PRINT
#define FUELGAUGE

#ifdef USE_SPI
ICM_20948_SPI myICM; // If using SPI create an ICM_20948_SPI object
#else
ICM_20948_I2C myICM; // Otherwise create an ICM_20948_I2C object
#endif

// Wifi creds
const char *ssid;
const char *password;
const char *host;  

const int network = 0; // 0 = Router, 1 = Adam's hotspot, 2 = Aiden's hotspot 
const int port = 1238;
int ports[4] = {1238, 1239, 1240, 1241};

void setup()
{
  SERIAL_PORT.begin(9600); // Start the serial console

const char *Aiden_laptop = "192.168.8.101";
const char *Evan_laptop = "192.168.8.162";
const char *Adam_laptop = "192.168.8.203";
const char *Adam_laptop_LAN = "192.168.8.148";
const char *Aiden_PC = "192.168.8.122";
const char *Aiden_laptop_LAN = "192.168.8.219";
const char *Aiden_PC_LAN = "192.168.8.132";

#ifdef TRANSMIT
  // Setting WiFi
  if (network == 0) {
    ssid = "Vestigo-Router";
    password = "Vestigo&2023";
    //host = Aiden_laptop; 
    // host = Evan_laptop;
    // host = Adam_laptop;
    // host = Aiden_PC;
    // host = Adam_laptop_LAN; 
    // host = Aiden_laptop_LAN;
    host = Aiden_PC_LAN;
  } 
  else if (network == 1){
    ssid = "UMAT_WiFi";
    password = "andito21";
    host = "192.168.106.177"; 
  
  } 
  else if (network == 2){
    ssid = "FREE WIFI NO MALWARE";
    password = "Playadel2005?";
    host = "192.168."; 
  }

  // Connecting to WiFi
  SERIAL_PORT.print("Connecting to ");
  SERIAL_PORT.println(ssid);
  WiFi.begin(ssid, password);
  while (WiFi.status() != WL_CONNECTED) {
    delay(1000);
    SERIAL_PORT.println("Connecting to Wifi... ");
  }
  SERIAL_PORT.println("Wifi connected");
#endif
#ifndef QUAT_ANIMATION
  SERIAL_PORT.println(F("ICM-20948 Example"));
#endif

#ifndef QUAT_ANIMATION
  while (SERIAL_PORT.available()) // Make sure the serial RX buffer is empty
    SERIAL_PORT.read();

  SERIAL_PORT.println(F("Press any key to continue..."));

  while (!SERIAL_PORT.available()) // Wait for the user to press a key (send any serial character)
    ;
#endif

#ifdef USE_SPI
  SPI_PORT.begin();
#else
  WIRE_PORT.begin();
  WIRE_PORT.setClock(400000);
#endif

#ifndef QUAT_ANIMATION
  //myICM.enableDebugging(); // Uncomment this line to enable helpful debug messages on Serial
#endif

  bool initialized = false;
  while (!initialized)
  {

    // Initialize the ICM-20948
    // If the DMP is enabled, .begin performs a minimal startup. We need to configure the sample mode etc. manually.
#ifdef USE_SPI
    myICM.begin(CS_PIN, SPI_PORT);
#else
    myICM.begin(WIRE_PORT, AD0_VAL);
#endif

#ifndef QUAT_ANIMATION
    SERIAL_PORT.print(F("Initialization of the sensor returned: "));
    SERIAL_PORT.println(myICM.statusString());
#endif
    if (myICM.status != ICM_20948_Stat_Ok)
    {
#ifndef QUAT_ANIMATION
      SERIAL_PORT.println(F("Trying again..."));
#endif
      delay(500);
    }
    else
    {
      initialized = true;
    }
  }

#ifndef QUAT_ANIMATION
  SERIAL_PORT.println(F("Device connected!"));
#endif

  bool success = false; // Use success to show if the DMP configuration was successful

  while (!success){
    success = true;
    // Initialize the DMP. initializeDMP is a weak function. You can overwrite it if you want to e.g. to change the sample rate
    success &= (myICM.initializeDMP() == ICM_20948_Stat_Ok);

    // DMP sensor options are defined in ICM_20948_DMP.h
    //    INV_ICM20948_SENSOR_ACCELEROMETER               (16-bit accel)
    //    INV_ICM20948_SENSOR_GYROSCOPE                   (16-bit gyro + 32-bit calibrated gyro)
    //    INV_ICM20948_SENSOR_RAW_ACCELEROMETER           (16-bit accel)
    //    INV_ICM20948_SENSOR_RAW_GYROSCOPE               (16-bit gyro + 32-bit calibrated gyro)
    //    INV_ICM20948_SENSOR_MAGNETIC_FIELD_UNCALIBRATED (16-bit compass)
    //    INV_ICM20948_SENSOR_GYROSCOPE_UNCALIBRATED      (16-bit gyro)
    //    INV_ICM20948_SENSOR_STEP_DETECTOR               (Pedometer Step Detector)
    //    INV_ICM20948_SENSOR_STEP_COUNTER                (Pedometer Step Detector)
    //    INV_ICM20948_SENSOR_GAME_ROTATION_VECTOR        (32-bit 6-axis quaternion)
    //    INV_ICM20948_SENSOR_ROTATION_VECTOR             (32-bit 9-axis quaternion + heading accuracy)
    //    INV_ICM20948_SENSOR_GEOMAGNETIC_ROTATION_VECTOR (32-bit Geomag RV + heading accuracy)
    //    INV_ICM20948_SENSOR_GEOMAGNETIC_FIELD           (32-bit calibrated compass)
    //    INV_ICM20948_SENSOR_GRAVITY                     (32-bit 6-axis quaternion)
    //    INV_ICM20948_SENSOR_LINEAR_ACCELERATION         (16-bit accel + 32-bit 6-axis quaternion)
    //    INV_ICM20948_SENSOR_ORIENTATION                 (32-bit 9-axis quaternion + heading accuracy)

    // Enable the DMP orientation sensor
    success &= (myICM.enableDMPSensor(INV_ICM20948_SENSOR_ORIENTATION) == ICM_20948_Stat_Ok);

    // Enable any additional sensors / features
    //success &= (myICM.enableDMPSensor(INV_ICM20948_SENSOR_RAW_GYROSCOPE) == ICM_20948_Stat_Ok);
    //success &= (myICM.enableDMPSensor(INV_ICM20948_SENSOR_RAW_ACCELEROMETER) == ICM_20948_Stat_Ok);
    //success &= (myICM.enableDMPSensor(INV_ICM20948_SENSOR_MAGNETIC_FIELD_UNCALIBRATED) == ICM_20948_Stat_Ok);

    // Configuring DMP to output data at multiple ODRs:
    // DMP is capable of outputting multiple sensor data at different rates to FIFO.
    // Setting value can be calculated as follows:
    // Value = (DMP running rate / ODR ) - 1
    // E.g. For a 5Hz ODR rate when DMP is running at 55Hz, value = (55/5) - 1 = 10.
    success &= (myICM.setDMPODRrate(DMP_ODR_Reg_Quat6, 0) == ICM_20948_Stat_Ok); // Set to the maximum // WHY THIS LINE!?
    //success &= (myICM.setDMPODRrate(DMP_ODR_Reg_Accel, 0) == ICM_20948_Stat_Ok); // Set to the maximum
    //success &= (myICM.setDMPODRrate(DMP_ODR_Reg_Gyro, 0) == ICM_20948_Stat_Ok); // Set to the maximum
    //success &= (myICM.setDMPODRrate(DMP_ODR_Reg_Gyro_Calibr, 0) == ICM_20948_Stat_Ok); // Set to the maximum
    //success &= (myICM.setDMPODRrate(DMP_ODR_Reg_Cpass, 0) == ICM_20948_Stat_Ok); // Set to the maximum
    //success &= (myICM.setDMPODRrate(DMP_ODR_Reg_Cpass_Calibr, 0) == ICM_20948_Stat_Ok); // Set to the maximum

    // Enable the FIFO
    success &= (myICM.enableFIFO() == ICM_20948_Stat_Ok);

    // Enable the DMP
    success &= (myICM.enableDMP() == ICM_20948_Stat_Ok);

    // Reset DMP
    success &= (myICM.resetDMP() == ICM_20948_Stat_Ok);

    // Reset FIFO
    success &= (myICM.resetFIFO() == ICM_20948_Stat_Ok);

    // Check success
    if (success)
    {
  #ifndef QUAT_ANIMATION
      SERIAL_PORT.println(F("DMP enabled!"));
  #endif
    }
    else
    {
      SERIAL_PORT.println(F("Enable DMP failed!"));
      SERIAL_PORT.println(F("Trying again..."));
      delay(500);
    }
  }

  // WAIT FOR SENSOR TO CALIBRATE (LOCK ONTO CORRECT ORIENTATION)
  int elapsedCalibration = 0;
  int calibrationTime = 30000;
  pinMode(LED_PIN, OUTPUT);
  while (elapsedCalibration <= calibrationTime){
    digitalWrite(LED_PIN, HIGH); // turn the LED on   
    delay(500);
    digitalWrite(LED_PIN, LOW); // turn the LED off  
    delay(500); 
    SERIAL_PORT.println(elapsedCalibration/1000);     
    elapsedCalibration += 1000;
  }
#ifdef FUELGAUGE
  // Set up the MAX17048 LiPo fuel gauge:
  if (lipo.begin() == false) // Connect to the MAX17048 using the default wire port
  {
    Serial.println(F("MAX17048 not detected. Please check wiring. Freezing."));
    while (1)
      ;
  }
#endif
}

float roll = 0;
float pitch = 0;
float yaw = 0;
float accX;
float accY;
float accZ;
unsigned long dt;
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

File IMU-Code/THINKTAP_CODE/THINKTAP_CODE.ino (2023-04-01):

//#include <Kalman.h>
#include "Kalman.h"
//#include <BasicLinearAlgebra.h>
using namespace BLA;
/****************************************************************
 * Example1_Basics.ino
 * ICM 20948 Arduino Library Demo
 * Use the default configuration to stream 9-axis IMU data
 * Owen Lyke @ SparkFun Electronics
 * Original Creation Date: April 17 2019
 *
 * Please see License.md for the license information.
 *
 * Distributed as-is; no warranty is given.
 ***************************************************************/
#include "ICM_20948.h" // Click here to get the library: http://librarymanager/All#SparkFun_ICM_20948_IMU
double dataRate = 100000.0;
double delayMS = 1000/dataRate;
double delta_t = delayMS/1000.0;
double xPos = 0;
double yPos = 0;
double zPos = 0;
double xVel = 0;
double yVel = 0;
double zVel = 0;

void FindVel(double xacc, double yacc, double zacc, double& xVel, double& yVel, double& zVel,double t) {
    xVel += (xacc+0)*t/1000.0;
    yVel += (yacc+0)*t/1000.0;
    zVel += 0*zacc*t/1000.0;
}
void FindPos(double xVel, double yVel, double zVel, double& xPos, double& yPos, double& zPos, double t) {
    xPos += xVel*t;
    yPos += yVel*t;
    zPos += 0*zVel*t;
}
//------------------------------------
/****       KALMAN PARAMETERS    ****/
//------------------------------------

// Dimensions of the matrices
#define Nstate 3 // length of the state vector
#define Nobs 3   // length of the measurement vector

// measurement std (to be characterized from your sensors)
#define n1 0.1 // noise on the 1st measurement component
#define n2 0.1 // noise on the 2nd measurement component 
#define n3 0.1 // noise on the 2nd measurement component 

// model std (~1/inertia). Freedom you give to relieve your evolution equation
#define m1 0.01
#define m2 0.02
#define m3 0.02

KALMAN<Nstate,Nobs> K; // your Kalman filter
BLA::Matrix<Nobs> obs; // observation vector

//#define USE_SPI       // Uncomment this to use SPI

#define SERIAL_PORT Serial

#define SPI_PORT SPI // Your desired SPI port.       Used only when "USE_SPI" is defined
#define CS_PIN 2     // Which pin you connect CS to. Used only when "USE_SPI" is defined

#define WIRE_PORT Wire // Your desired Wire port.      Used when "USE_SPI" is not defined
// The value of the last bit of the I2C address.
// On the SparkFun 9DoF IMU breakout the default is 1, and when the ADR jumper is closed the value becomes 0
#define AD0_VAL 1

#ifdef USE_SPI
ICM_20948_SPI myICM; // If using SPI create an ICM_20948_SPI object
#else
ICM_20948_I2C myICM; // Otherwise create an ICM_20948_I2C object
#endif



void setup()
{
  // example of evolution matrix. Size is <Nstate,Nstate>
  K.F = {1.0, delta_t, 0.5 * delta_t * delta_t,
         0.0, 1.0, delta_t,
         0.0, 0.0, 1.0};
  // example of measurement matrix. Size is <Nobs,Nstate>
  K.H = {1.0, 0.0,
         0.0, 1.0};
  // example of measurement covariance matrix. Size is <Nobs,Nobs>
  K.R = {n1*n1,   0.0, 0.0,
           0.0, n2*n2, 0.0,
           0.0, 0.0, n3*n3};
  // example of model covariance matrix. Size is <Nstate,Nstate>
  K.Q = {m1*m1,   0.0, 0.0,
           0.0, m2*m2, 0.0,
           0.0, 0.0, m3*m3};

    // Initialize the process noise covariance matrix

  SERIAL_PORT.begin(115200);
  while (!SERIAL_PORT)
  {
  };

#ifdef USE_SPI
  SPI_PORT.begin();
#else
  WIRE_PORT.begin();
  WIRE_PORT.setClock(400000);
#endif

  //myICM.enableDebugging(); // Uncomment this line to enable helpful debug messages on Serial

  bool initialized = false;
  while (!initialized)
  {

#ifdef USE_SPI
    myICM.begin(CS_PIN, SPI_PORT);
#else
    myICM.begin(WIRE_PORT, AD0_VAL);
#endif

    SERIAL_PORT.print(F("Initialization of the sensor returned: "));
    SERIAL_PORT.println(myICM.statusString());
    if (myICM.status != ICM_20948_Stat_Ok)
    {
      SERIAL_PORT.println("Trying again...");
      delay(500);
    }
    else
    {
      initialized = true;
    }
  }
}

void loop()
{

  if (myICM.dataReady())
  {
    myICM.getAGMT();         // The values are only updated when you call 'getAGMT'
                             //    printRawAGMT( myICM.agmt );     // Uncomment this to see the raw values, taken directly from the agmt structure
    printScaledAGMT(&myICM); // This function takes into account the scale settings from when the measurement was made to calculate the values with units
    
    
    delay(delayMS); // originally 30.0
  }
  else
  {
    SERIAL_PORT.println("Waiting for data");
    delay(500);
  }
  

}

// Below here are some helper functions to print the data nicely!


//dude.VelocityUpdate(sensor->accX,sensor->accY,sensor->accZ);
//dude.PositionUpdate(dude.xVel, dude.yVel, dude.zVel);
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

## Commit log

2023-04-02 Working on Orientation
    - Creating MatLAB script to read serial port data from IMU and write to text file
    - Currently takes in 1000 readings, and I've created a graph in excel displaying the roll, pitch, and yaw
    [euler_data.xlsx]
2023-04-03 Gravity Tests & Patch
    - Uploading data from gravity tests (3 tests, each with gravity in a different axis) as well as our patch
    [GravityX.xlsx, GravityY.xlsx, GravityZ.xlsx, euler_data.xlsx]
2023-04-05 WiFi Functionality (MQTT & ThingSpeak), LiPo Fuel Gauge
    - Uploaded lipo battery fuel gauge code from the Thing Plus hookup guide
    - Successfully trasmitted data wirelessly from the ESP to ThingSpeak, but it was limited to 1 transmission every 15 sec, so had to figure something else out
    - Tried using MQTT, with HiveMQ and Mosquitto, but haven't quite figure it out yet
2023-04-08 IMU Data Transmission over UDP
    - Got IMU data transfer working over WiFi (using UDP port 1221)
    [GravityX.xlsx, GravityY.xlsx, GravityZ.xlsx]
2023-04-10 Gravity & Accelerometer Calibration
    - Figured out formula for calculating gravity components using roll, pitch, and yaw
    - Ran multiple tests to verify data and calibrate accelerometer data
    - Code is more of less ready to run and transmit data (roll, pitch, yaw, ax, ay, az, dt)
    [euler_acceleration_gravity_data.xlsx, euler_and_acceleration_data.xlsx, euler_data.xlsx]
2023-04-11 IMU Position Attempt
    - Position data not looking very good so far, will work on calibrating and trying to find ways to improve
    [euler_acceleration_gravity_data.xlsx]
2023-04-11 Fixed UWB
    - Tweaked code to make sure UWB still works
    - Improved calibration of IMU accelerometer
    [euler_acceleration_gravity_data.xlsx]
2023-04-12 Partially Complete Kalman Filter
    - Only have some of the Kalman Filter implemented so far
    [euler_data.xlsx]
2023-04-12 Update main.cpp
    - Still working on Kalman Filter
2023-04-19 File Update
    - Implemented LiPo Fuel Gauge in The IMU Code
    - Added a bunch of test data
    - ALSO WE WON!!!
    [IMU_Data_Test.xlsx, UWBFullPositionTest.xlsx, euler_acceleration_gravity_data.xlsx]
2023-05-23 PCB Information
    Prototype PCB Schematic (just has the CAD for each component right now) as well as data sheet of each component
    [Prototype Board.sch]
2023-05-30 Removed Receiver Mode on Tag
    Begin to develop ESP NOW Comm network.
    10 hz transmission speed
2023-05-31 WiFi Socket to Gateway Connection
2023-06-04 PCB Updates
    [Pins.xlsx]
2023-06-04 Partially connected the IMU unit to the ESP32
    Might need level shifting, haven't tied all the pins yet
    [Prototype Board.sch]
2023-06-07 Added Level Shifting, Updated Power Supply, Finished Connecting Components
    The core schematic is almost done, may need some additional touches for optional functionality. Once this is done, we can proceed to route all the connections (e.g. commit to the board file)
    [Prototype Board.sch]
2023-06-18 Began laying out components on the board
    We're going to need a 4 layered board and fine trace control, which means we'll probably have to order from JCBPCL rather than use the FEDC fabs.
    [Prototype Board.brd, Prototype Board.sch, PrototypeBOM.csv]
2023-06-21 Re-Labeled Code Base to New Naming Scheme
    [GravityX.xlsx, GravityY.xlsx, GravityZ.xlsx, IMU_Data_Test.xlsx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]
2023-06-21 Refactored Repo to Match New Naming Scheme
    [GravityX.xlsx, GravityY.xlsx, GravityZ.xlsx, IMU_Data_Test.xlsx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]
2023-06-24 Added Testing Prints
2023-06-24 Removed Extra Print Statements
2023-06-25 Commented Out Print Statements
2023-06-26 Syntax Updates
    Removed All Print Statements
    Updates pollPreviousTag to function properly
2023-06-27 Refactor files
    [Anchor on Top.SLDPRT]
2023-07-12 Grouped Schematic
    Components selected, laid out, not routed yet
    [Prototype Board.brd, Prototype Board.sch]
2023-07-21 Board Almost Finished
    Need to route IO connectors, retouch design rules, clean up connections, etc
    [Prototype Board bad routing.brd, Prototype Board bad routing.sch, Prototype Board.brd, Prototype Board.sch]
2023-07-21 Resolved half of the warnings
    Will need to look into the USB footprint. Looks odd
    [Prototype Board.brd, Prototype Board.sch]
2023-07-25 Resolved all DRC violations
    [Prototype Board.brd, Prototype Board.sch]
2023-07-31 Completed First Draft of PCB + Assembly Details
    [BOM.csv, CPL.csv, CPL.xlsx, Prototype Board.brd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]
2023-08-06 Finalized PCB
    [BOM.csv, CPL.xlsx, EconomyBOM.csv, EconomyCPL.csv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]
2023-08-08 Large Update
    Switched to only use Eigen (much cleaner in most cases)
    Reduced repetitive sections
    Removed socket connection
    Added serial connection
    Improved LMA slightly (more robust SVD)
    Removed redundant code
2023-09-25 Setting up Qt
    - Decided to try switching from SDL to Qt, which apparently has its own IDA (Qt Creator)
    - Wrote a script to generate random data points into a csv
    - Set up a test project inside Qt Creator and got the main.cpp script to successfully read the csv file (had to figure out how to change the working directory)
    [simdata.csv]
2023-10-06 Folder Rename
    - Renamed Visualization Tool to GUI
    [simdata.csv]
2023-10-11 Added timestamps and serial printing
2023-10-11 Print Statements for TWR Mod
2023-10-16 Basic Kalman Filter
2023-10-21 Qt WIP Update
    - Uploading some work in progress (WIP) Qt Code
    - Revised IMU_SIM_CODE into TAG_SIM_CODE, to send data over serial
    [simdata.csv]
2023-10-28 Kalman filter implemented, Compiles
2023-10-28 Fixed Master average ToF error
    Error is likely low sample count and random noise in the system.
    Added several checks which should prevent large average ToFs
2023-10-29 Removed Kalman Filter and Added Simple Linear Model
    Doesn't work as intended as far as I can tell.
    Corrected Time Cycles between 3 times. Time Difference is also off by a constant.
    Times decay when not synced
    Delta Time fixed
    Startup issues fixed
    Variable Type fix WIP
    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
2023-11-05 Major GUI Update
    - Created vestigo-gui, where the GUI is currently being built
    - Created 3 classes (with corresponding header and cpp files): tagData, mapWidget, and crewMember
    - Currently taking in live data from serial port, calculating position using Root Finder, and displaying it at a frequency around 0.66 Hz (relatively slow)
    - Data is being recorded to an output csv named with MM:DD:YY
    [11-4-2023.csv, euler_acceleration_gravity_data.xlsx]
2023-11-06 GUI Live Visualization
    - 2 Floors visualized, with 4 TAGs represented by circles
    - Circles color coded and colors shown in legend
    - Timestamp is also displayed (HH:MM:SS)
    - TAG locations displaying in status bar
    - Black background
    - Updated TAG_SIM_CODE
    [11-4-2023.csv, 11-5-2023.csv]
2023-11-08 GUI with da tabs
    - Added tabs to switch between Live Visualization, Playback, Summary
    - Added button to start and stop visualization
    - Incorporated summary scene, which generates density maps and data analytics
    - Fixed issues with graphics displayed only every other data point (by changing timer from updating as fast as possible, to doing so every 100 milliseconds)
    [11-7-2023.csv, percentage_output.csv]
2023-11-08 Bypass Serial Port Connection
    - Updated code to not automatically try to connect to serial port upon startup, allowing users to use it without sensors connected
    [11-7-2023.csv]
2023-11-12 summary scene updates
    Added summary scene functionality, density map is not appearing on GUI screen though.
    [12Hr_TestRun.csv_output.csv]
2023-11-12 Revert "summary scene updates"
    This reverts commit 26f43b9502bab87772243ab7c2394805c06e05db.
    [12Hr_TestRun.csv_output.csv]
2023-11-12 Revert "Bypass Serial Port Connection"
    This reverts commit fb2a9edea38c8aa1b849ab34f9eefb08589b44d2.
    [11-7-2023.csv]

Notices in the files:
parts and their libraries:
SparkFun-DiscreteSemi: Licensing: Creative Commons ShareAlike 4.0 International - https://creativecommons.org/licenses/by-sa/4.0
